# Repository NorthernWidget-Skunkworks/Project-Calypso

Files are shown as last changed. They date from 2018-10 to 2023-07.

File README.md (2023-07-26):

# Project-Calypso
The hardware and software designs for a turbidity measurement system, based on the work of a 2018 UMN senior design team

## Project Summary

Our team developed an open-source sensor to measure water turbidity. Turbidity, or "murkiness", increases when the water carries more sediment. Dissolved compounds can also increase turbidity by reducing water clarity. In general, less suspended and dissolved material makes better drinking water. Anyone may download and build this sensor (Design: https://doi.org/10.5281/zenodo.8177929).

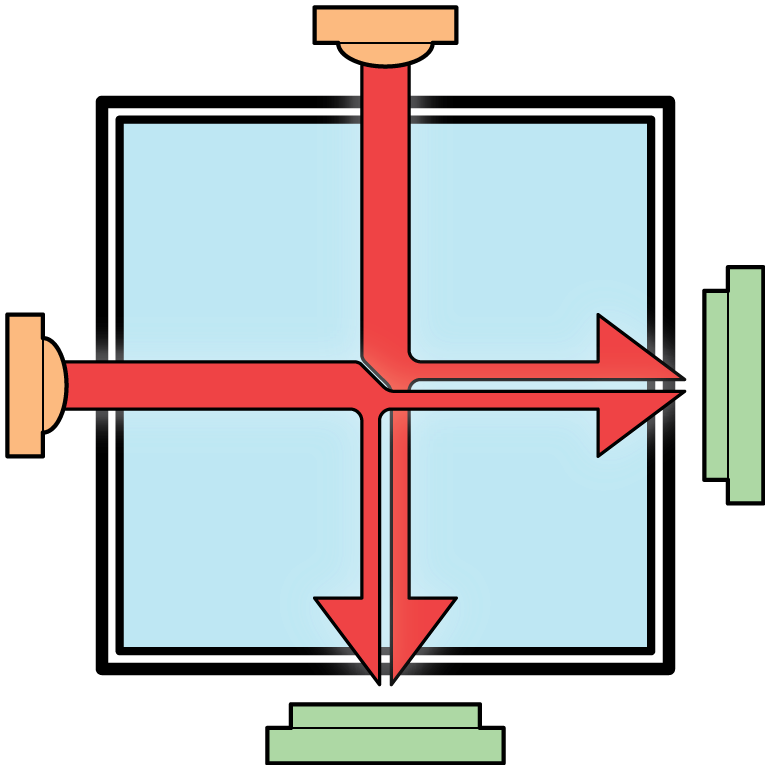
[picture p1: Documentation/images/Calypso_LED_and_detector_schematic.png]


*Two LEDs, red and infrared, send beams across the water to be measured, which lies within a transparent tube. These LED beams interact with the water, which reduces transmission and increases sidewas scatter. The detectors record both changes.*

The sensor, called "Project Calypso", shines lights from two LEDs through the water. These LEDs lie at right angles from each other along a clear square plastic tube. Detectors record the LEDs' brightness. The sensor directly across from each LED records light transmission. The sensor at 90 degrees from each LED records light scattering. Sediment in the water blocks the light and reduces transmission. Light can reflect off of sediment and scatter onto the sensor at 90 degrees. The scattering pattern depends on the wavelength of the light and sediment size. Therefore, we use both visible (red) and infrared light to learn about sediment size. Dissolved material reduces light transmission but does not scatter the light sideways. Because of this, Project Calypso can differentiate between sediment and dissolved compounds.

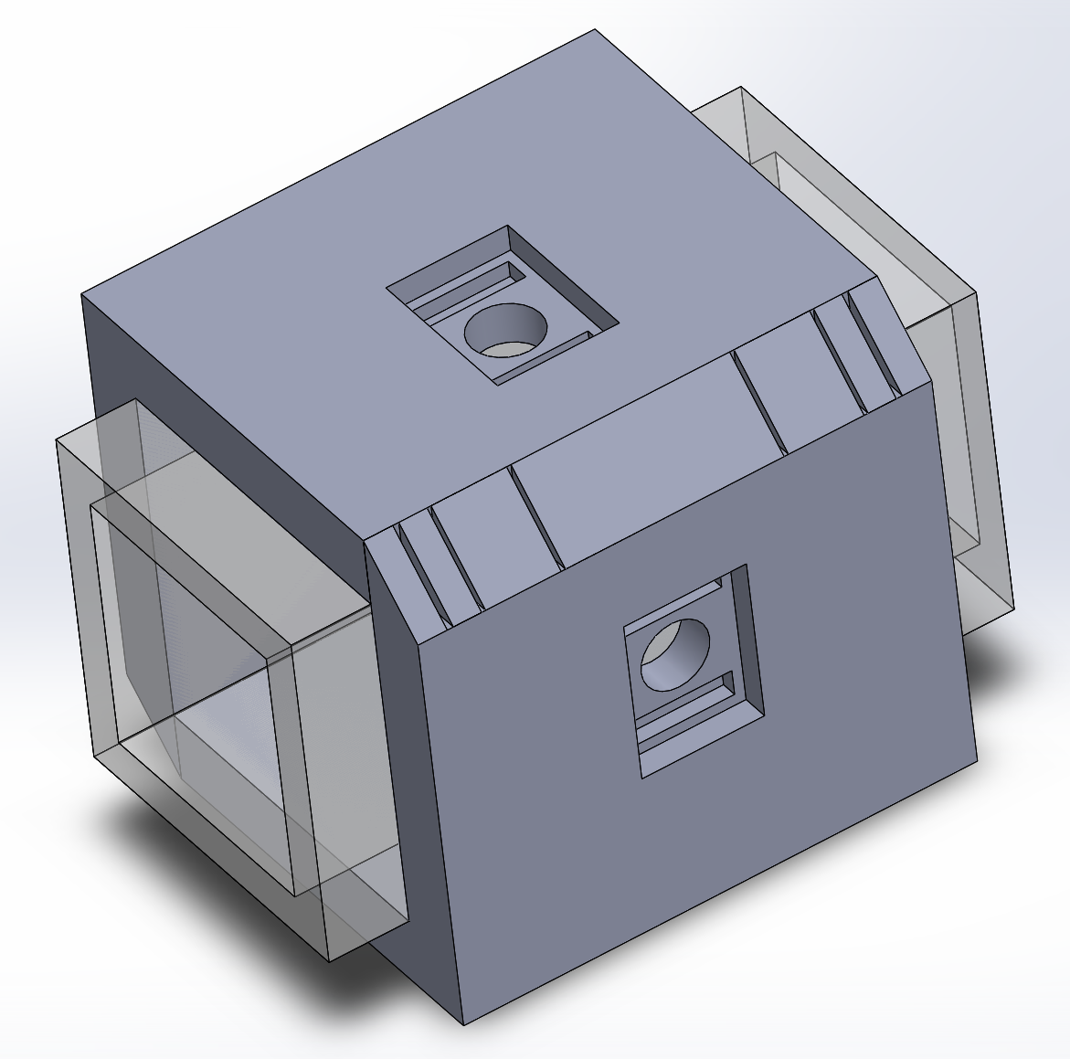
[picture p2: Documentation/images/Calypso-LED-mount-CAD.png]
CAD drawing of the LED and detector mount


*CAD drawing of the LED and detector mount. Sensors and mount surround a transparent plastic tube with a square cross section. Water, along with any suspended and/or dissolved matter that it carries, fills this tube.*

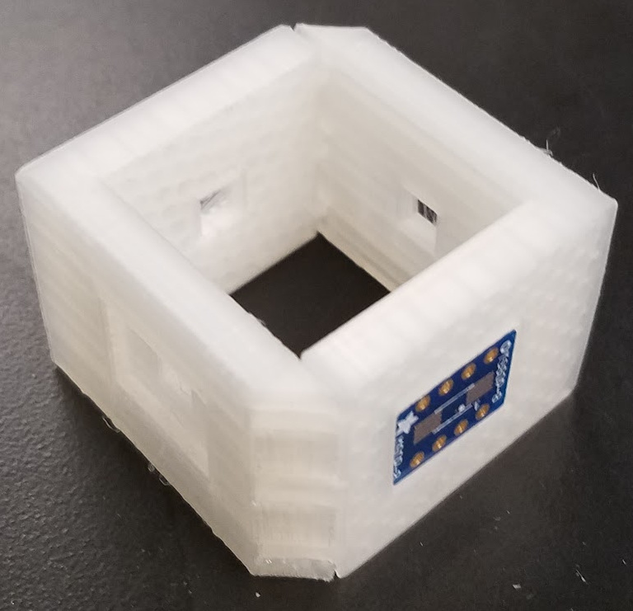
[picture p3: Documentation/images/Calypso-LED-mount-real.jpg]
Image of the LED and detector mount, including installed circuit boards.


*3-D printed LED and detctor mount, along with one of the installed custom circuit boards to hold the LEDs and light detectors.*

We characterized the Calypso sensor using standards of known turbidity. Sensor response varied systematically with water cloudiness and light wavelength. The Calypso turbidity-sensor system is not only an open-source alternative. It also provides more information than standard turbidity sensors.

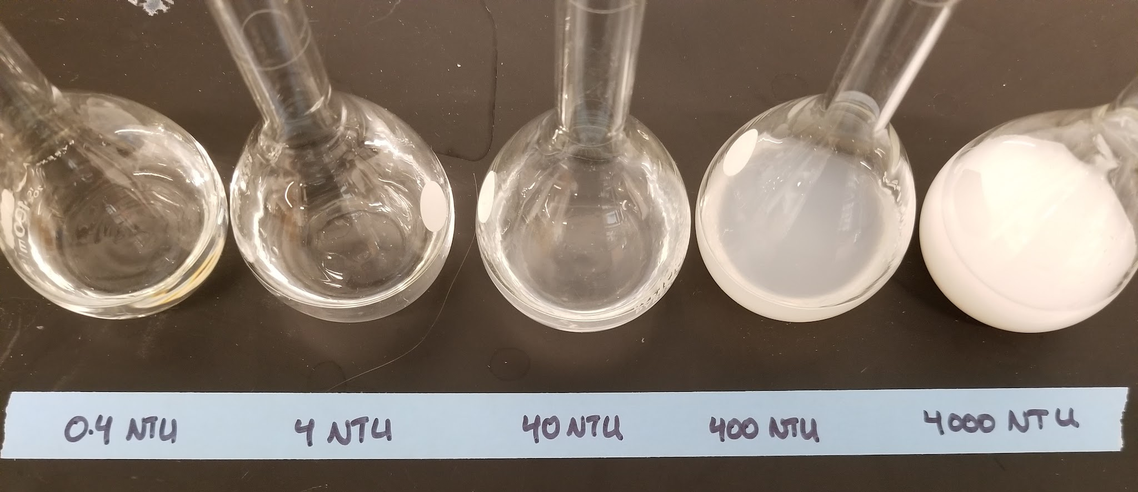
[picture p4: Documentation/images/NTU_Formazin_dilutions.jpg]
Increasing concentrations of Formaizin (left to right), with water becoming systematically cloudier.


*Increasing concentrations of Formaizin (left to right) cause the water to become systematically cloudier. We characterized the sensor using these standards.*

## Funding Support

Funding for this work came from the ***University of Minnesota Water Resources Center***, with support from the **USGS WRRI** program. This funding supported a grant to Wickert, Sandell, and Karwan, for their proposal entitled, *Open-Source Turbidity Sensor to Monitor Suspended and Dissolved Matter in Surface Water*.

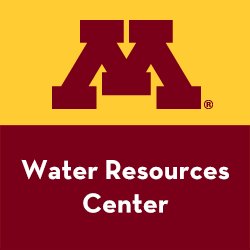
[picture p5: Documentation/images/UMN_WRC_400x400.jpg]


<br/>
<br />This work is licensed under a <a rel="license" href="http://creativecommons.org/licenses/by-sa/4.0/">Creative Commons Attribution-ShareAlike 4.0 International License</a>.

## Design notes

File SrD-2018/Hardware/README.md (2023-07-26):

# Senior Design 2018

Design files for the functional prototype designed by the student team and led by Bobby Schulz, Andy Wickert, Chad Sandell, and Diana Karwan.

Students:
* Corbin Buechler
* Amanda Hayden
* Aaron Nightingale
* Sean Rogers
* Erik Sundberg
* Jacob Wolf

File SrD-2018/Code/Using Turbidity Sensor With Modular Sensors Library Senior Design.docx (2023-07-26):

Turbidity Sensor & Modular Sensors Library

By Aaron Nightingale (night030@umn.edu)

Summary:

The turbidity sensor made for the spring 2018 senior design project can communicate with any device running the modular sensors library (like the MayFly data logger). This is accomplished using the “Turbidity.h” and “TurbidityHelper.h” classes. This document will describe how to set up this sensor with the modular sensors library. In addition, this document will explain various functions in each class, and how to use them.

Adding a Turbidity Sensor

This section will walk you through adding a turbidity sensor to the data logger code. See “MayFly-Logging => turbidity_logging => turbidity_logging.ino” for an example of using the turbidity sensor with the modular sensors library on the MayFly data logger (In the “Code Backups” folder on the Google drive).

1. Change the logging interval to be 10 minutes or more. For example:

const float loggingInterval = 10.0;

2. Include the “Turbidity.h” and “TurbidityHelper.h” classes:

#include "Turbidity.h"

#include "TurbidityHelper.h"

3. Add these constants to define the sensor’s address and the power pin:
  - Note: The turbidity sensor’s slave I2C address can be changed by altering the code found in “turbidity_slave.ino”.

uint8_t Turbidityi2c_addr = 0x08;

const int I2CPower = 22;

4. Create new “Turbidity” and “TurbidityHelper” objects as follows:
  - Note: The turbidity class had to be split up into two separate classes. This is because the turbidity sensor logs 7 different variables, and there is a limit of 4 variables per class in the modular sensors library.

Turbidity ntu01(I2CPower, Turbidityi2c_addr);

TurbidityHelper ntu02(I2CPower, Turbidityi2c_addr);

5. Add the following objects to the “variableList” array. These will be logged to an SD card.

new Turbidity_FS(&ntu01),

new Turbidity_SS(&ntu01),

new Turbidity_DARK(&ntu01),

new Turbidity_NTU(&ntu01),

new TurbidityHelper_FS(&ntu02),

new TurbidityHelper_SS(&ntu02),

new TurbidityHelper_DARK(&ntu02),

6. Congratulations! The turbidity sensor is now ready to be used with the MayFly. Upload the program to the MayFly, and connect the turbidity sensor to the data logger as shown in figure 1 below:

Data Logger Connection | Turbidity Sensor Connection | Purpose
+3.3v | Red | Sensor power
GND | Black | Sensor ground
(SDA) | Blue | I2C data line
(SCL) | Yellow | I2C clock line
N / A | Green | Sensor busy pin (Optional)

Figure 1 - Connections between the data logger and the turbidity sensor

“Turbidity.h” Class Reference

Summary

The “Turbidity.h” class is responsible for reading data from the turbidity sensor, telling the turbidity sensor to take a new measurement (update), and logging four of seven variables. This class is used in conjunction with “TurbidityHelper.h” to log all of the turbidity sensor’s data. The constants and functions in this class are described below:

Constants

- #define TURBIDITY_NUM_VARIABLES 4
  - This defines the number of variables in the “Turbidity.h” class. These four variables will be logged to an SD card.
- #define TURBIDITY_WARM_UP_TIME_MS 100
  - This defines the number of milliseconds necessary for the turbidity sensor to properly start up. 100ms was chosen as a “safe guestimate”.
- #define TURBIDITY_STABILIZATION_TIME_MS 0
  - This is the stabilization time for the turbidity sensor. This is unused in our setup.
- #define TURBIDITY_MEASUREMENT_TIME_MS 1000
  - This parameter defines the measurement time of the sensor. The default value of 1s was used.
- #define TURBIDITY_FS_RESOLUTION 2
  - This parameter sets the precision of the logged variable. In this case, the Turbidity_FS variable will be logged as a float with 2 digits past the decimal point.
- #define TURBIDITY_FS_VAR_NUM 0
  - This constant defines which variable is in position 0 of the variable array. In this case, the forward scattered light variable (from LED #1) is in position 0.
- #define TURBIDITY_SS_RESOLUTION 2
  - This parameter sets the precision of the logged variable. In this case, the Turbidity_SS variable will be logged as a float with 2 digits past the decimal point.
- #define TURBIDITY_SS_VAR_NUM 1
  - This constant defines which variable is in position 1 of the variable array. In this case, the side scattered light variable (from LED #1) is in position 1.
- #define TURBIDITY_DARK_RESOLUTION 2
  - This parameter sets the precision of the logged variable. In this case, the Turbidity_Dark variable will be logged as a float with 2 digits past the decimal point.
- #define TURBIDITY_DARK_VAR_NUM 2
  - This constant defines which variable is in position 2 of the variable array. In this case, the dark counts variable (from sensor #1) is in position 2.
- #define TURBIDITY_NTU_RESOLUTION 2
  - This parameter sets the precision of the logged variable. In this case, the Turbidity_NTU variable will be logged as a float with 2 digits past the decimal point.
- #define TURBIDITY_NTU_VAR_NUM 3
  - This constant defines which variable is in position 3 of the variable array. In this case, the turbidity variable (NTU) is in position 3.
- #define DATA_LEN 6
  - This constant defines the size of the response from the turbidity sensor. The turbidity sensor sends 6 float-type variables, causing the data length constant to be 6.
- #define COMMAND_LEN 7
  - The data logger can send various commands to the turbidity sensor. The commands are sent as a character array, and the length of said array is 7 bytes. Note that the last byte must be a zero.
- #define RES_DARK1 0
  - The turbidity sensor returns an array of 6 float-type variables to the datalogger. The float at position 0 of this array is the number of dark counts from sensor #1. The units for this are Hertz.
- #define RES_TRAN1 2
  - The turbidity sensor returns an array of 6 float-type variables to the datalogger. The float at position 2 of this array is the number of transmission counts from LED #1. The units for this are Hertz.
- #define RES_SCAT1 3
  - The turbidity sensor returns an array of 6 float-type variables to the datalogger. The float at position 3 of this array is the number of side scatter counts from LED #1. The units for this are Hertz.
- #define RES_DARK2 1
  - The turbidity sensor returns an array of 6 float-type variables to the datalogger. The float at position 1 of this array is the number of dark counts from sensor #2. The units for this are Hertz.
- #define RES_TRAN2 4
  - The turbidity sensor returns an array of 6 float-type variables to the datalogger. The float at position 4 of this array is the number of transmission counts from LED #2. The units for this are Hertz.
- #define RES_SCAT2 5
  - The turbidity sensor returns an array of 6 float-type variables to the datalogger. The float at position 5 of this array is the number of side scatter counts from LED #2. The units for this are Hertz.

Class Members

- uint8_t _i2cAddressHex;
  - This variable contains the I2C address of the turbidity slave sensor.
- char command[COMMAND_LEN];
  - This array contains the command that will be sent to the turbidity sensor. This array is a character array.
- float response[DATA_LEN];
  - This array contains the response from the turbidity sensor. This array consists of 6 float-type variables. Using these 6 variables, the turbidity of the water can be calculated. The variable at each position of the array is given by the “RES_XXX” constants. (Note that RES stands for RESponse array).

Class Methods

- Turbidity(int powerPin, uint8_t i2cAddressHex = 0x08, int

measurementsToAverage = 1);

  - This is the constructor for the “Turbidity.h” class. In this function, the “i2cAddressHex” variable is saved to the “_i2cAddressHex” member variable.
- bool wake(void) override;
  - This function is executed whenever the sensor is “waked” after a period of being idle. This function basically makes sure the sensor is powered on, and that the sensor has waited the proper warm up time.
- SENSOR_STATUS setup(void) override;
  - This function is executed whenever the sensor is set up for the first time. This function doesn’t do anything, and only returns the value of “getStatus()”.
- SENSOR_STATUS getStatus(void) override;
  - This function makes sure that the sensor is powered on. Then, this function checks to make sure that there is an I2C slave device at the “_i2cAddressHex” address. If there are any errors in either of these processes, the “SENSOR_ERROR” flag is returned. If the sensor was set up successfully, the “SENSOR_READY” flag is returned.
- String getSensorLocation(void) override;
  - This function returns a string containing the I2C address of the sensor. For example, “I2C_0x08”.
- bool addSingleMeasurementResult(void) override;
  - This function begins by calling the “sensorRead()” function. This function fills the “response[]” array with the current measurements from the turbidity sensor. Next, the values from the response array are copied to the “sensorValues[]” array. This allows the readings to be logged later. Afterwards, the “updateCommand()” is called to tell the sensor to take a new reading. This measurement process takes up to 8 minutes. Finally, the function returns true upon completion.
- bool sensorPresent();
  - This function verifies that a sensor is present at the current I2C address specified by the variable “_i2cAddressHex”. If a sensor is not present, this function returns false. If a sensor is present, the function returns true.
- void sensorRead();
  - This function reads data from the slave turbidity sensor over I2C. This is done in a byte by byte process, and the results are stored in the float-type “response[]” array.
- void sensorWrite();
  - This function sends the contents of the “command[]” array to the slave turbidity sensor. By changing the contents of the “command[]” array, different commands can be sent to the turbidity sensor. For example, if the array consists of “{‘U’,’P’,’D’,’A’,’T’,’E’,0}, then the update command is issued and the turbidity sensor begins taking a new measurement.
- void updateCommand();
  - This function sets the contents of the “command[]” array to be {‘U’,’P’,’D’,’A’,’T’,’E’,0}. Then the “sensorWrite()” function is called to send the update command to the turbidity sensor. This command tells the turbidity sensor to start taking a new measurement.
- float calculate_turbidity(float data[6]);
  - The “response[]” array should be passed to this function. This function calculates the turbidity using the data in the “response[]” array. The turbidity is returned as a float-type variable. This function can be changed to more accurately calibrate the turbidity sensor.

“TurbidityHelper.h” Class Reference

Summary

The turbidity sensor needs to log 7 variables to an SD card. However, the modular sensors library only allows 4 variables to be logged per sensor. To get around this, the “TurbidityHelper.h” class is used. This class is responsible for logging the side scatter counts from LED #2, the forward transmission counts from LED #2, and the dark counts from sensor #2. This class is very similar to the “Turbidity.h” class.

Constants

- #define TURBIDITY_HELPER_NUM_VARIABLES 3
  - This constant defines the number of variables that will be logged to an SD card using the modular sensors library.
- #define TURBIDITY_HELPER_WARM_UP_TIME_MS 100
  - This parameter defines the warm up time (in milliseconds) for the turbidity sensor. The default value of 100ms was used.
- #define TURBIDITY_HELPER_STABILIZATION_TIME_MS 0
  - This parameter defines the stabilization time (in milliseconds) for the turbidity sensor. The default value of 0ms was used.
- #define TURBIDITY_HELPER_MEASUREMENT_TIME_MS 1000
  - This constant defines the measurement time in milliseconds. The default value of 1s was used.
- #define TURBIDITY_HELPER_FS_RESOLUTION 2
  - This constant defines how many digits will be after the decimal point when saving the forward scattered light measurement to an SD card.
- #define TURBIDITY_HELPER_FS_VAR_NUM 0
  - This constant defines which variable is in position 0 of the variable array. In this case, the forward scatter counts variable (from LED #2) is in position 2.
- #define TURBIDITY_HELPER_SS_RESOLUTION 2
  - This constant defines how many digits will be after the decimal point when saving the side scattered light measurement to an SD card.
- #define TURBIDITY_HELPER_SS_VAR_NUM 1
  - This constant defines which variable is in position 1 of the variable array. In this case, the side scatter counts variable (from LED #2) is in position 1.
- #define TURBIDITY_HELPER_DARK_RESOLUTION 2
  - This constant defines how many digits will be after the decimal point when saving the dark counts measurement to an SD card.
- #define TURBIDITY_HELPER_DARK_VAR_NUM 2
  - This constant defines which variable is in position 2 of the variable array. In this case, the dark counts variable (from sensor #2) is in position 2.
- #define DATA_LEN 6
  - This constant defines the size of the response from the turbidity sensor. The turbidity sensor sends 6 float-type variables, causing the data length constant to be 6.
- #define RES_DARK1 0
  - The turbidity sensor returns an array of 6 float-type variables to the datalogger. The float at position 0 of this array is the number of dark counts from sensor #1. The units for this are Hertz.
- #define RES_TRAN1 2
  - The turbidity sensor returns an array of 6 float-type variables to the datalogger. The float at position 2 of this array is the number of transmission counts from LED #1. The units for this are Hertz.
- #define RES_SCAT1 3
  - The turbidity sensor returns an array of 6 float-type variables to the datalogger. The float at position 3 of this array is the number of side scatter counts from LED #1. The units for this are Hertz.
- #define RES_DARK2 1
  - The turbidity sensor returns an array of 6 float-type variables to the datalogger. The float at position 1 of this array is the number of dark counts from sensor #2. The units for this are Hertz.
- #define RES_TRAN2 4
  - The turbidity sensor returns an array of 6 float-type variables to the datalogger. The float at position 4 of this array is the number of transmission counts from LED #2. The units for this are Hertz.
- #define RES_SCAT2 5
  - The turbidity sensor returns an array of 6 float-type variables to the datalogger. The float at position 5 of this array is the number of side scatter counts from LED #2. The units for this are Hertz.

Class Members

- uint8_t _i2cAddressHex;
  - This variable contains the I2C address of the turbidity slave sensor.
- float response[DATA_LEN];
  - This array contains the response from the turbidity sensor. This array consists of 6 float-type variables. Using these 6 variables, the turbidity of the water can be calculated. The variable at each position of the array is given by the “RES_XXX” constants. (Note that RES stands for RESponse array).

Class Methods

- Turbidity(int powerPin, uint8_t i2cAddressHex = 0x08, int

measurementsToAverage = 1);

  - This is the constructor for the “Turbidity.h” class. In this function, the “i2cAddressHex” variable is saved to the “_i2cAddressHex” member variable.
- bool wake(void) override;
  - This function is executed whenever the sensor is “waked” after a period of being idle. This function basically makes sure the sensor is powered on, and that the sensor has waited the proper warm up time.
- SENSOR_STATUS setup(void) override;
  - This function is executed whenever the sensor is set up for the first time. This function doesn’t do anything, and only returns the value of “getStatus()”.
- SENSOR_STATUS getStatus(void) override;
  - This function makes sure that the sensor is powered on. Then, this function checks to make sure that there is an I2C slave device at the “_i2cAddressHex” address. If there are any errors in either of these processes, the “SENSOR_ERROR” flag is returned. If the sensor was set up successfully, the “SENSOR_READY” flag is returned.
- String getSensorLocation(void) override;
  - This function returns a string containing the I2C address of the sensor. For example, “I2C_0x08”.
- bool addSingleMeasurementResult(void) override;
  - This function begins by calling the “sensorRead()” function. This function fills the “response[]” array with the current measurements from the turbidity sensor. Next, the values from the response array are copied to the “sensorValues[]” array. This allows the readings to be logged later. Finally, the function returns true upon completion.
- bool sensorPresent();
  - This function verifies that a sensor is present at the current I2C address specified by the variable “_i2cAddressHex”. If a sensor is not present, this function returns false. If a sensor is present, the function returns true.
- void sensorRead();
  - This function reads data from the slave turbidity sensor over I2C. This is done in a byte by byte process, and the results are stored in the float-type “response[]” array.

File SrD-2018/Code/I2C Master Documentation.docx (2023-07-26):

I2C Master Documentation

By Aaron Nightingale (night030@umn.edu)

Summary:

The program titled “i2c-master.ino” is a bare-bones program that enables an Arduino to act as an I2C master device, and request readings from the turbidity sensor (slave device). This program is much easier to understand than the “Turbidity.h” and “TurbidityHelper.h” classes which are based on the modular sensors library. This program was frequently used when testing the turbidity sensor.

Using This Program

This program was used to test the turbidity sensor and do simple demonstrations. This program is intended to be programmed to an Arduino, which acts like a master device. Using this program, the Arduino can tell the turbidity sensor to take a new reading and display the results of that measurement on the serial monitor.

1. To use this program, upload it to a 3.3v Arduino device. (Note that 5v Arduinos could be used as well, but a level shifter is required. Figure 1 shows the type of level shifter that was used in our preliminary prototyping).
  - NXP has great documentation on I2C level shifters. General purpose N-Channel MOSFETS like the 2N7000 can be used. See the following website for more information:
  - https://www.nxp.com/docs/en/application-note/AN10441.pdf
2. Next, unplug the Arduino from the computer, and connect it to the turbidity sensor. The connections are shown in figure 2 below.
3. Verify the connections, and plug the Arduino back into the computer.
4. Select the serial port corresponding to the master Arduino. Then open the serial monitor and set the baud rate to 9600 bit/s.
5. You should see “Sensor #8 found.” displayed on the serial monitor. If not, double check the wiring, and make sure that the turbidity sensor is programmed with the “turbidity_slave.ino” program.
6. Various commands can now be sent to the turbidity sensor. For example, type “UPDATE” into the text box of the serial monitor and press enter. This will tell the turbidity sensor to take a new turbidity measurement.
7. The measurement process takes about 8 minutes. Once it is complete, the measurement results are displayed on the serial monitor. This includes the calculated water turbidity in NTU.
8. Now the turbidity sensor is up and running, and communicating with an I2C “master” Arduino!

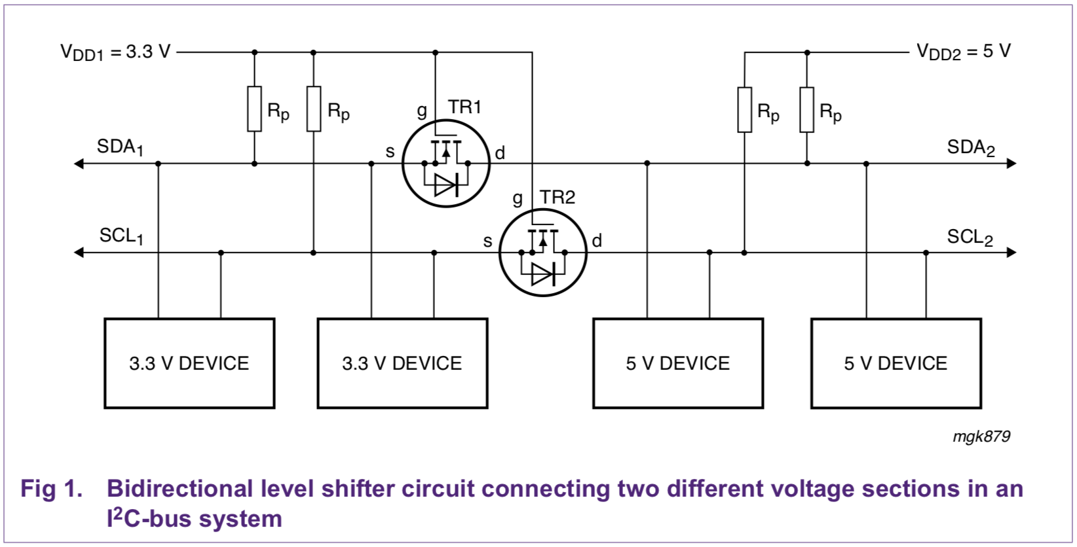
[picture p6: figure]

Figure 1 - I2C level shifter circuit

Master Arduino Connection | Turbidity Sensor Connection | Purpose
+3.3v | Red | Sensor power
GND | Black | Sensor ground
A4 (SDA) | Blue | I2C data line
A5 (SCL) | Yellow | I2C clock line
N / A | Green | Sensor busy pin (Optional)

Figure 2 - Connections between the I2C master Arduino and the turbidity sensor

“i2c-master.ino” Reference

Constants

- #define SLAVE_ADDR 8
  - This constant defines the address of the turbidity sensor. If the address of the turbidity sensor is changed in “turbidity_slave.ino”, then this constant must be changed to properly communicate with the turbidity sensor.
- #define DATA_LEN 6
  - This constant defines the size of the response from the turbidity sensor. The turbidity sensor sends 6 float-type variables, causing the data length constant to be 6.
- #define COMMAND_LEN 7
  - The data logger can send various commands to the turbidity sensor. The commands are sent as a character array, and the length of said array is 7 bytes. Note that the last byte must be a zero.
- #define RES_DARK1 0
  - The turbidity sensor returns an array of 6 float-type variables to the datalogger. The float at position 0 of this array is the number of dark counts from sensor #1. The units for this are Hertz.
- #define RES_TRAN1 2
  - The turbidity sensor returns an array of 6 float-type variables to the datalogger. The float at position 2 of this array is the number of transmission counts from LED #1. The units for this are Hertz.
- #define RES_SCAT1 3
  - The turbidity sensor returns an array of 6 float-type variables to the datalogger. The float at position 3 of this array is the number of side scatter counts from LED #1. The units for this are Hertz.
- #define RES_DARK2 1
  - The turbidity sensor returns an array of 6 float-type variables to the datalogger. The float at position 1 of this array is the number of dark counts from sensor #2. The units for this are Hertz.
- #define RES_TRAN2 4
  - The turbidity sensor returns an array of 6 float-type variables to the datalogger. The float at position 4 of this array is the number of transmission counts from LED #2. The units for this are Hertz.
- #define RES_SCAT2 5
  - The turbidity sensor returns an array of 6 float-type variables to the datalogger. The float at position 5 of this array is the number of side scatter counts from LED #2. The units for this are Hertz.

Global Variables

- char command[COMMAND_LEN];
  - This array contains the command that will be sent to the turbidity sensor. This array is a character array.
- float response[DATA_LEN];
  - This array contains the response from the turbidity sensor. This array consists of 6 float-type variables. Using these 6 variables, the turbidity of the water can be calculated. The variable at each position of the array is given by the “RES_XXX” constants. (Note that RES stands for RESponse array).

Functions

- void setup()
  - This is the setup function of the I2C master program. In this function, the I2C bus and the serial port are initialized. After that, the function checks to see if there is a turbidity sensor connected to the I2C bus using the “sensorPresent()” function.
- void loop()
  - This is the main loop of the program. The function begins by reading the current values of the sensor using the “sensorRead()” function. Next, this data is displayed on the serial monitor using the “dumpFormattedData()” function. Afterwards, the program waits until the user has entered a command into the serial monitor. If a valid command is entered, then this command is sent to the turbidity sensor using I2C. In most cases, the “UPDATE” command is sent to the turbidity sensor, causing it to take a new turbidity reading. This measurement process takes about 8 minutes, so an 8 minute delay is added to this function. Then, the function loops back to the start and repeats.
- void getSerialCommand()
  - When this program is running, and the master Arduino device is connected to a computer, then the user may send commands to the turbidity sensor using the serial monitor. This function reads data from the serial monitor and puts it into the “command[]” array. For example, if a user types “UPDATE” into the serial monitor, then this function parses that string into a character array {‘U’,’P’,’D’,’A’,’T’,’E’,’0’}, which can be sent to the turbidity sensor using I2C.
- bool sensorPresent(int addr)
  - This function checks if there is a sensor present at the desired address. This function is used before any data transactions with the turbidity sensor. TRUE is returned if an I2C sensor was found at the specified address.
- void sensorRead()
  - This function requests data from the turbidity sensor using I2C. The turbidity sensor sends 6 float-type variables one byte at a time. This function reads the data from the turbidity sensor, byte by byte, and stores this data in the “response[]” array.
- void sensorWrite()
  - This function sends the contents of the “command[]” array to the slave turbidity sensor. By changing the contents of the “command[]” array, different commands can be sent to the turbidity sensor. For example, if the array consists of “{‘U’,’P’,’D’,’A’,’T’,’E’,0}, then the update command is issued and the turbidity sensor begins taking a new measurement.
- void debug(int i)
  - This is a basic function that is used for debugging. When this function is called, “DEBUG: #” is written to the serial monitor, where the value if the argument “i” is represented by the # sign.
- void dumpSensorData()
  - This function dumps the contents of the “response[]” array to the serial monitor. Each float is displayed on a new line. This function was primarily used for debugging purposes.
- float calculate_turbidity()
  - This function calculates the turbidity using the data in the “response[]” array. The turbidity is returned as a float-type variable. This function can be changed to more accurately calibrate the turbidity sensor.
- void dumpFormattedData()
  - This function dumps the contents of the “response[]” array to the serial monitor. However, unlike the “dumpSensorData()” function, this function displays a short description of what each number is. This function was used for debugging and simple demonstrations of the turbidity sensor.

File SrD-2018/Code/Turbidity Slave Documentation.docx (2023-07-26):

Turbidity Slave Documentation

By Aaron Nightingale (night030@umn.edu)

Summary:

This program contains the code for a turbidity sensor. The turbidity sensor is an I2C slave device, and can communicate with another Arduino or data logger using I2C. This turbidity slave program contains functions that measure the transmitted light, scattered light, and the dark counts from each light-to-frequency sensor. In addition, this program has functions that average these readings and sends them to a master I2C device.

Using This Program

1. Open the “turbidity_slave.ino” program in the Arduino IDE.
2. Next, upload this program to a 3.3v compatible ATMega328 chip.
  - Notice: You may need to burn the bootloader to the chip first. See the following link for details on how to do that:
  - https://www.arduino.cc/en/Tutorial/ArduinoToBreadboard
3. Once the program has been uploaded to the chip, connect the chip to the turbidity sensor circuitry. (Schematics of this circuitry can be found in the following Google Drive folder: “Turbidity Sensor Senior Design 2018” => “Final Documentation”)
4. Double check the circuit connections.
5. Now the turbidity sensor is ready to be used! Connect the turbidity sensor to a 3.3v Arduino running the “i2c-master.ino” program to view the turbidity measurements.
  - For reference, the connections are shown in figure 1 below:
  - See “I2C Master Documentation” PDF for more details on how to set this up.

Master Arduino Connection | Turbidity Sensor Connection | Purpose
+3.3v | Red | Sensor power
GND | Black | Sensor ground
A4 (SDA) | Blue | I2C data line
A5 (SCL) | Yellow | I2C clock line
N / A | Green | Sensor busy pin (Optional)

Figure 2 - Connections between the I2C master Arduino and the turbidity sensor

“turbidity_slave.ino” Reference

Constants

- #define SLAVE_ADDR 8
  - This constant defines the address of the turbidity sensor. If the address of the turbidity sensor is changed in “turbidity_slave.ino”, then this constant must be changed to properly communicate with the turbidity sensor.
- #define DATA_LEN 6
  - This constant defines the size of the response from the turbidity sensor. The turbidity sensor sends 6 float-type variables, causing the data length constant to be 6.
- #define COMMAND_LEN 7
  - The data logger can send various commands to the turbidity sensor. The commands are sent as a character array, and the length of said array is 7 bytes. Note that the last byte must be a zero.
- #define SENSOR1 2
  - This parameter defines the pin that is connected to sensor #1. (Light to frequency sensor #1).
- #define SENSOR2 3
  - This parameter defines the pin that is connected to sensor #2. (Light to frequency sensor #2).
- #define L1_HIGH 5
  - This parameter defines the pin that controls when LED #1 is turned on.
- #define L1_OFF 6
  - This constant defines the pin that controls when LED #1 is turned off.
- #define L2_HIGH 7
  - This parameter defines the pin that controls when LED #2 is turned on.
- #define L2_OFF 8
  - This constant defines the pin that controls when LED #2 is turned off.
- #define BUSY 13
  - This constant defines the location of the busy pin. This pin is held high when the turbidity sensor is busy taking a new measurement. The turbidity sensor should not be interrupted over I2C while a measurement is in progress.
- #define TYPES 6
  - This parameter defines the size of the array which stores the measurement results. The turbidity sensor measures 6 different parameters, which are stored in the “result[]” array.
- #define REPEATS 5
  - This parameter defines the number of measurements that should be averaged for each new reading.
- const char MODE01[] = {'M','O','D','E','0','1',0};
  - This constant defines the “MODE01” I2C command. This command is not implemented in the turbidity sensor, but can be used as an example of how to implement custom I2C commands into the program.
- const char MODE02[] = {'M','O','D','E','0','2',0};
  - This constant defines the “MODE02” I2C command. This command is not implemented in the turbidity sensor, but can be used as an example of how to implement custom I2C commands into the program.
- const char MODE03[] = {'M','O','D','E','0','3',0};
  - This constant defines the “MODE03” I2C command. This command is not implemented in the turbidity sensor, but can be used as an example of how to implement custom I2C commands into the program.
- const char UPDATE[] = {'U','P','D','A','T','E',0};
  - This constant defines the “UPDATE” command. This command tells the turbidity sensor to take a new turbidity reading.

Global Variables

- char command[COMMAND_LEN];
  - This array contains the command that will be sent to the turbidity sensor. This array is a character array.
- volatile uint8_t go;
  - This variable stores the number of seconds remaining in the frequency measurement process.
- volatile uint32_t count;
  - This variable stores the number of rising edges that were counted on the interrupt pin.
- float measurements[TYPES][REPEATS]
  - This array holds all of the measurements from the light to frequency sensors. The “TYPES” dimension corresponds to the different measurements, while the “REPEATS” dimension corresponds to separate sets of measurements. The “REPEATS” dimension is usually 5, meaning that 5 measurements are averaged. The average of the measurements in this array is stored in the “result[]” array, which is then sent to the data logger.
- float result[TYPES];
  - This array contains the response from the turbidity sensor. This array consists of 6 float-type variables. Using these 6 variables, the turbidity of the water can be calculated. The contents of this array are sent to the I2C master device (data logger) over I2C in a byte by byte process.
- bool needsUpdate;
  - This variable is TRUE whenever the sensor needs to take a new measurement. Long functions cannot be used in the I2C interrupt routines, which is why this variable is used.

Functions

- void setup()
  - This function is run before the main loop. It initializes the I2C interface and sets up the timers used for measurements. The input and output pins are set in this function as well.
- ISR(TIMER1_COMPA_vect)
  - This is an interrupt service routine for timer #1 within the Arduino microcontroller. This routine is called whenever the value in the timer register is equal to the value of some compare register. This function is used to measure the counts on the light to frequency sensors for some duration of seconds.
- void freq_counter()
  - This function is also an interrupt routine, and is called whenever there is a rising edge on some pin. This function simply increments the “count” variable with each rising edge. This function can be used on different pins of the Arduino microcontroller using the “attachInterrupt()” function.
- void LED1_OFF()
  - This function sets the “L1_OFF” pin high in order to turn LED #1 off.
- void LED1_LOW()
  - This function sets LED #1 to the low-intensity setting. This is done by setting the “L1_OFF” pin and the “L1_HIGH” pin low.
- void LED1_HIGH()
  - This function sets LED #1 to the high-intensity setting. This is done by setting the “L1_HIGH” pin high and setting the “L1_OFF” pin low.
- void LED2_OFF()
  - This function sets the “L2_OFF” pin high in order to turn LED #2 off.
- void LED2_LOW()
  - This function sets LED #2 to the low-intensity setting. This is done by setting the “L2_OFF” pin and the “L2_HIGH” pin low.
- void LED2_HIGH()
  - This function sets LED #2 to the high-intensity setting. This is done by setting the “L2_HIGH” pin high and setting the “L2_OFF” pin low.
- uint32_t SENSE1(uint8_t seconds)
  - This function reads the pulses from light-to-frequency sensor #1. The pulses are counted for a time duration specified in the argument of the function. The number of pulses counted is returned as an unsigned 32 bit integer.
- uint32_t SENSE2(uint8_t seconds)
  - This function reads the pulses from light-to-frequency sensor #2. The pulses are counted for a time duration specified in the argument of the function. The number of pulses counted is returned as an unsigned 32 bit integer.
- float READ_SENSOR1()
  - This function uses the “SENSE1()” function to calculate the frequency of the pulses from sensor #1. The frequency of the pulses from light-to-frequency sensor #1 is returned as a float-type variable.
- float READ_SENSOR2()
  - This function uses the “SENSE2()” function to calculate the frequency of the pulses from sensor #2. The frequency of the pulses from light-to-frequency sensor #2 is returned as a float-type variable.
- float SENSOR1_DARK()
  - This function turns each LED off, and measures the frequency from light-to-frequency sensor #1. The frequency is returned as a float-type variable.
- float SENSOR2_DARK()
  - This function turns each LED off, and measures the frequency from light-to-frequency sensor #2. The frequency is returned as a float-type variable.
- float LED1_TRANSMISSION()
  - This function measures the transmitted light from LED #1. This is done by setting LED #1 to be in the low intensity mode. This is accomplished using the “LED1_LOW()” function. Afterwards, the frequency is measured using the “READ_SENSOR1()” function. The intensity of the transmitted light is proportional to the frequency of the light-to-frequency sensor, which is returned as a float-type variable in hertz.
  - Note: Increasing the brightness of the LED can cause the light-to-frequency sensor to produce more pulses than the microcontroller can handle. For this reason, the LED has a low intensity mode.
- float LED1_SCATTER()
  - This function measures the 90˚ side-scattered light from LED #1. To do this, LED #1 is set to operate in the high-intensity mode. This is done by calling the “LED1_HIGH()” function. Next, the frequency of the light-to-frequency sensor is measured using the “READ_SENSOR2()” command. The intensity of the side-scattered light is proportional to the frequency of the light-to-frequency sensor, which is returned as a float-type variable in hertz.
- float LED2_TRANSMISSION()
  - This function measures the transmitted light from LED #2. This is done by setting LED #2 to be in the low intensity mode. This is accomplished using the “LED1_LOW()” function. Afterwards, the frequency is measured using the “READ_SENSOR2()” function. The intensity of the transmitted light is proportional to the frequency of the light-to-frequency sensor, which is returned as a float-type variable in hertz.
  - Note: Increasing the brightness of the LED can cause the light-to-frequency sensor to produce more pulses than the microcontroller can handle. For this reason, the LED has a low intensity mode.
- float LED2_SCATTER()
  - This function measures the 90˚ side-scattered light from LED #2. To do this, LED #2 is set to operate in the high-intensity mode. This is done by calling the “LED2_HIGH()” function. Next, the frequency of the light-to-frequency sensor is measured using the “READ_SENSOR1()” command. The intensity of the side-scattered light is proportional to the frequency of the light-to-frequency sensor, which is returned as a float-type variable in hertz.
- void measure()
  - This function measures the dark counts, transmitted light, and the side scattered light from each light-to-frequency sensor. This is a total of 6 frequency measurements, which are saved to the “measurements[][]” array. These measurements are repeated several times, as specified by the “REPEATS” constant. In our setup, 5 sets of measurements are taken each time that this function is called.
- void average()
  - This function calculates the average frequency of each of the 6 different frequency measurements (dark counts, transmission, side scatter, etc.). The average values are saved to the “result[]” array, and are later sent to the data logger over I2C.
- void requestEvent()
  - This function is an interrupt service routine for the I2C interface. This function is called whenever the master device requests data from the turbidity sensor. This function sends the contents of the “result[]” array, byte by byte, to the master device using the I2C interface.
- void receiveEvent(int howMany)
  - This function is an interrupt service routine for the I2C interface. This function is called whenever the master sends data to the turbidity sensor. The data logger can send various commands to the turbidity sensor. This function interprets and executes the received command.
  - The only command that is implemented right now is the “UPDATE” command. When the turbidity sensor receives the character array corresponding to this command over I2C, the “needsUpdate” variable is set to be true. This causes the turbidity sensor to take a new set of measurements.
- void loop()
  - This is the main loop of the turbidity sensor program. In this loop, the turbidity sensor takes a new set of measurements if the “needsUpdate” variable is true. After the new measurements are taken and averaged, the “needsUpdate” variable is set to false. This loop waits 1ms and then repeats itself.

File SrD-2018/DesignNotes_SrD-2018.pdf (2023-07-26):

Solidworks Models: The final models are included in a seperate folder with some easy to open images. The curves are visual approximations, however, most of the dimensions are direct from the manufacturer. The gasket wasn’t modeled. The 3D printed part is the same as the final one Bobby sent. The 45 degree angle cut of the 3D printed part isn’t necessary should the hole for the acrylic tube be moved slightly further away from the short edge of the box. Ideally, one should use the black filament version of the one Bobby was using to keep reflections to a minimum. ABS is not recommended due to warping and worse tolerancing.

Breakout Boards: The final breakout boards, though slightly more expensive, had pads that better fit the LEDs and IR sensors. They were also smaller and had only 6 pins instead of the 8 from the Adafruit.

Measurement Routine: The turbidity sensor collects a total of six measurements: Sensor 1 dark, Sensor 2 dark, LED 1 transmission, LED 1 side scatter, LED 2 transmission, and LED 2 side scatter. The dark measurements are collected with both LEDs off to determine the amount of ambient light present to use as a baseline for the other measurements. In all of our code and documentation LEDs and Sensors are numbered so that LED 1 faces Sensor 1, and LED 2 faces Sensor 2. Therefore, the LED 1 transmission measurement is collected by Sensor 1 and its side scatter is collected by Sensor 2, and so on.

Since the sensors can output a maximum frequency of almost 600 kHz, but the ATmega329P microcontroller can only count edges on a signal up to 75 kHz (when it is clocked at 8 MHz), the SN74HC393N binary counter sits between the sensors and the microcontroller to effectively divide the incoming frequencies by 8. While this configuration allows the full range of the light sensors to be utilized, it also introduces a potential error since the microcontroller is only counting every eighth rising edge. This error is inversely proportional to the number of edges that are counted, so low frequencies are most affected. To address this, the functions controlling the measurement process make adjustments to try to receive at least 100 edges for each sample, which ensures an error of less than one percent.

For each measurement, the microcontroller first samples the sensor output for one second. If it receives 100 or more edges (corresponding to frequencies of 800 Hz and higher), it accepts this value. If it receives less than 100 edges, it determines the amount of time needed to receive 100 edges, with some additional headroom, and samples again for this extended amount of time. For example, if the microcontroller receives 37 pulses in one second, it will repeat for three seconds on the second pass. If less than three pulses are received in the first pass, the second pass is collected for the maximum length of two minutes. This will allow the microcontroller to detect frequencies as low as 5.87 Hz with a 1% error maximum error. As will be discussed below, this will correspond to a maximum expected collection time of about 8.5 minutes. If it is preferred to collect data more often, the maximum sampling time can be reduced at the expense of some precision. For example, if the maximum sampling time is reduced to one minute or 30 seconds, the minimum frequency detected at 1% error or less would be increased to 11.73 Hz or 27.47 Hz, respectively, with maximum expected collections times of about 4.5 minutes and 2.5 minutes, respectively.

Since the two dark measurements are the only ones that tend to be below the 800 Hz threshold, and are therefore the primary drivers of the collection length, they are not collected as often as the other four measurements in a cycle. The routine begins by collecting each of the two dark measurements, followed by five passes of the other four (two transmission and two side scatters), and then finishes with another collection of the two dark measurements. This means that there are a total of four dark measurements, which can take up to two minutes each depending on the amount of ambient light present, plus twenty transmission and side scatter measurements, which are very rarely longer than one second each. This results in the roughly 8.5 minute maximum collection time mentioned above. The six sets of measurements are then averaged so that only six values are reported to the data logger. The data logger computes the conversion to NTU and logs this value along with the six that were reported by the sensor.

Calibration Process: To calibrate the sensor, we collected measurements using six samples of varying turbidity - deionized water (treated as 0.0004 NTU for fit lines), 0.4 NTU, 4 NTU, 40 NTU, 400 NTU, and 4000 NTU. In the accompanying “Calibration” folder, we have provided the raw data from these measurements. The resulting best fit lines from our calibration process are listed below. Due to some saturation/non-linear behavior in our data, certain sections of the curves were not used to generate the fit lines. Since the side-scatter from LED 1 is fit from 0.0004 NTU to 400 NTU, this frequency value is used by the conversion function to determine what range of turbidity we are dealing with and therefore which formulas should be calculated and averaged to determine the NTU value.

LED 1 Side Scatter for < 4 NTU
NTU = 10^((freq-4884.51015963563)/(217.615730769231))

LED 1 Side Scatter for 4-400 NTU
NTU = (freq-4723.4758127632)/(112.799965681699)

LED 1 Transmission for > 400 NTU
NTU = exp((freq-905841.461548272)/(-108472.245937816))

LED 2 Side Scatter for 4-400 NTU
NTU = (freq-6696.20138888889)/(79.3873036786787)

LED 2 Transmission > 400 NTU
NTU = exp((freq-601607.276911029)/(-71291.2384864573))

Before applying these formulas, the dark measurement taken from the corresponding sensor is subtracted from the transmission or side scatter measurement. For example, if an LED 2 side scatter measurement is 10,160.00 Hz, and the Sensor 1 dark measurement is 73.85 Hz, then the difference, 10,086.15 Hz, is used in the NTU conversion formula. We determined that this is an accurate method for controlling for ambient light by measuring each calibration sample five times with regular lighting conditions and five times with an additional light shining into the turbidity sensor’s tube. We found that the dark and transmission/side scatter measurements from collected from a light sensor would increase by the same number of hertz, with the difference between them remaining constant.

Possible Extension - LEDs Supplied by Current Sources: As Bobby has brought up, an alternative to our design with fixed resistors setting the current through the LEDs would be to implement a digitally or PWM controlled current source to drive the LEDs instead. This would allow the light intensities to be adjusted after a sensor is constructed, which would not only help with tuning an individual sensor to maximize its accuracy but would also be able to address variations from unit to unit due to the manufacturing process once the sensors are being produced in larger quantities. We did not get a chance to look into this alternative extensively during the semester and have not identified any specific hardware to implement, but if we were going to continue working on this project, this would be the next direction that we would explore.

Possible Extension - LEDs of Different Wavelengths: Since our design essentially collects redundant data from the two identical light sources, a possible extension would be to experiment with changing the wavelength of one of the LEDs. While researching the light sources recommended for measuring turbidity, we found that that the 860 nm wavelength that we implemented works best for the most common particle size of interest. By using a different wavelength with one of the LEDs, the sensor could measure the turbidity due to two different particle sizes in the water. We were not able to find any other wavelength recommendations, so we do not know if it would be most useful to increase or decrease the wavelength or by how much, but we believe that this is another possible area where the sensor’s capability could be improved with some additional research.

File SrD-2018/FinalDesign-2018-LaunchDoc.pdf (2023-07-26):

### Turbidity Sensor Product Launch Document

University of Minnesota
EE 4951W
May 2, 2018

Group Members:
Corbin Buechler
Amanda Hayden
Aaron Nightingale
Sean Rogers
Erik Sundberg
Jacob Wolf

Advisors:
Professor Joseph Talghader - Electrical and Computer Engineering Professor Andrew Wickert - Department of Earth Sciences Anthony Aufdenkampe - Senior Environmental Scientist, LimnoTech

Abstract/Summary

Turbidity, the cloudiness or haziness of a fluid, is a major symptom of water pollution in all bodies of water, and it is only getting worse. Detecting water turbidity levels in remote locations is challenging and expensive, and it is often not feasible. Our team has developed a portable and inexpensive turbidity sensor that will work with multiple open source data loggers. The crucial components of the sensor include its waterproof housing, the light source, light detecting circuitry, and the software responsible for relaying data to the open source data logger. After these individual parts were designed, they were integrated into a final product that can be left in remote locations for data acquisition. Researchers hope that this sensor will be able to be reproduced on a larger scale to help monitor and mitigate turbidity levels in rivers, lakes, streams, and perhaps even drinking water in developing countries.

Introduction

This paper addresses the following areas of the project; motivation, objectives and customer requirements, technical background, design and description, team organization, overall goals, future improvements, timeline, and budget. The motivation for the project is simple, to develop a low cost and portable turbidity sensor that can be used with multiple open source data loggers and be deployed for lengthy periods of time. The technical background gives the reader an understanding of what a turbidity sensor is and how it operates. The design and description includes details of development of the main parts of the design. The first major component being the LED and sensor circuit that contains the light to frequency converters and software that correlates the frequency to some turbidity measurement. The second major component being the I2C communications interface between our sensor and the data logger. The third major component is the circuit design and layout. In particular, the LEDs and sensors had to be accurately positioned in order to optimize the light passing through the acrylic tube. The last major component is the waterproof housing and cable, as well as the overall integration of each component. In regards to team organization, we chose to delegate different components of the project to each person. Although each person was responsible for a different part of the project, there was a lot of collaboration in order to integrate the final product. The goal of the project very closely followed the initial specifications and requirements of the client. Although the project was successful, there are some changes that could be implemented if the design were to be reproduced, mostly having to do with time and monetary constraints. As for the timeline, the integration of all parts began the last week in March to allow significant time for testing and calibration that were to be completed by May 1st. The development costs came in under budget, at around $750. In addition, the final sensor design costs less than $100, as requested.

Motivation

Given that Minnesota has thousands of lakes and streams, water turbidity is a serious problem locally. However, measuring it is difficult. There is not enough time and resources to test all bodies of water. Sensors that are available are expensive, often costing over $1,000. To make matters worse, most commercial sensors are designed to be used in a lab setting, meaning researchers and scientists cannot take measurements in the field. Lab sensors also require calibration using special solutions, which significantly increases the cost. The sensors that can give real-time readings are even more expensive, so much so that it is not fiscally viable for a company to purchase more than one or two of these units. This project proposed the development of a low-cost turbidity sensor that can be field deployed in remote locations. In turn, this sensor will help quantify and mitigate the effect of practices that lead to contamination and soil loss. Our turbidity sensor uses low amounts of power, and can be powered from a solar cell in field testing situations. The turbidity sensor also communicates with an open-source data logger, which saves the turbidity readings onto an SD card. This allows researchers to have access to real-time turbidity readings without having to bring samples or the sensor back to the lab. All of the designs for this turbidity sensor are open-source, allowing other researchers to build their own turbidity sensor and continue the development of the design. When the design and documentation is made available, this project could lead to massive changes in environmental research and protection.

Objectives and Customer Requirements

The main goal of this project is to create a working turbidity meter, loosely following a design provided by the client. The sensor shall use light scattering and transmission to measure the turbidity of water. The clients currently use two different data-loggers for field measurements. Another goal of this project was to write code that interfaced our sensor with these open source data loggers. The client required that all sensor and communications code must be open-source for future changes and use.
The client provided several overall project specifications as well. First, a working turbidity sensor must be developed, prototyped, and delivered to the client by the end of the semester. In addition, the fully operational sensor must be shown at the senior design show. The sensor should be able to correctly read the turbidity of various liquids in a blind test. The clients would provide us with a budget of $1,000. We were expected to get approval and place all purchases through their lab, with the exception of minor circuit components, which could be obtained from the ECE Depot if possible.
Because the client would like to use this sensor in the field, there are several important specifications for the device itself. Foremost, it must be enclosed in a rugged, waterproof enclosure that can withstand up to three months of deployment in typical bodies of water. For that reason, it must be IP68 rated. For example, it must be able to withstand currents pushing it around and any possible impacts from debris churned up during storms or other events. It must have the minimum power consumption possible for prolonged operation. The enclosure must also be able to handle depths of up to three meters. The sensor is being powered from a solar panel mounted on a central box nearby. There are other instruments inside this box that also draw power. It is important that our sensor does not overload this box. Our client uses sensors that draw a maximum of 50 mA, so the current consumption of our sensor should be below that. The sensor must operate on 5 and/or 3.3 volts, as that is the only power provided from the box. The sensor itself must use a light source (LED or laser) to measure scattering at different angles and transmission, in order to better calculate the NTU of the water in question. The sensor code within must be modeled in Arduino in order to be compatible the data loggers. All final code must be open source as well. Calibration, using standard turbidity liquids must be performed, and should be done in a lab setting. The sensors will report readings in Nephelometric Turbidity Units (NTU) with an accuracy of 3%. The target price per sensor should be less than $100. Diana Karwan, the co-lead client for this project, would like to test a unit in the field in April, depending on weather.
The client has also requested several pieces of paperwork along with a working sensor. First, they would like a bill of materials in order to see a breakdown of required parts and costs to manufacture several sensors. Next, they have also requested instructions on how to build the sensor. These must be simple enough so that anyone can follow them. Along with the instructions, the clients would like information regarding important design decisions made throughout the project. This will make it easier for the client to make further changes or improvements, based on difficulties we experienced during our development and prototyping.

Technical Background

The most commonly used unit of measurement for turbidity is the Nephelometric Turbidity Unit (NTU). Turbidity is determined by shining a beam of light through the liquid sample and measuring the amount of light that is scattered at some angle. The most common arrangements measure 90 degree side-scattering, backscattering, which is the light reflected back toward the source, or transmission, which is the light that passes through the sample in a straight line from the source. Many commercial turbidity meters measure only a single direction of light scattering, which can perform well in measuring low turbidity samples but are less accurate past a certain threshold NTU. In more turbid conditions, the light may be scattered multiple times, causing less of it to reach the sensor, which would be interpreted as a decrease in turbidity. By measuring both light scattering and transmission, a sensor can take accurate readings over a wider range of turbidity values. As discussed below, our sensor measures the light transmitted and the light scattered at 90 degrees from two different light sources.

Detailed Design Description

The exterior of the turbidity sensor consists of a waterproof aluminum box with a square acrylic water inlet tube mounted horizontally through the enclosure. Two infrared LEDs and two light intensity sensors are mounted around this square tube so that each LED faces one of the sensors. This arrangement allows the sensors to pick up the transmitted light and the 90 degree side-scattered light from each of the light sources. The LEDs used in our design have a wavelength of 860 nm, which was chosen to comply with the ISO 7027 standard for measuring turbidity. For light detection, we decided to use a pair of integrated circuits that senses light and outputs a square wave what a frequency that is proportional to the light intensity. These signals are collected by an ATmega328P microcontroller, which counts the number of rising edges over a period of time to determine the frequency. In most cases, this measurement is taken over one second, but it can be extended to up to two minutes to ensure that very low frequencies are counted accurately. Since the light sensors can output frequencies up to nearly 600 kHz, while the microcontroller’s interrupts can only reach up to 75 kHz, the light sensors’ outputs are routed through a pair of binary counters that effectively divide the output frequencies by eight before they reach the microcontroller’s inputs. This process introduces a potential error when collecting low frequency signals, but this is minimized by extending the sampling period in these cases.
In addition to capturing the outputs from the light intensity sensors, the ATmega chip also turns the LEDs on and off at the appropriate times. Since the maximum side-scattered light from a source is significantly less than the maximum transmitted light, we have developed a circuit that can light up each LED at a higher and a lower intensity to use as much of the light sensors’ range as possible. The sensing routine first measures the amount of ambient light present by measuring the outputs of each sensor with both LEDs off. Next, it turns one LED on with a low intensity, and capture the transmitted light data from the sensor directly across from it. Next, that same LED is turned up to the higher intensity, and side-scattered light data will be read from the other sensor, positioned at a 90 degree angle. This is then repeated for the other LED source. This process repeats five times for each of these four lights measurements followed by a final ambient light measurement. These six collected values are then each averaged and stored until they can be sent to the connected data logger via I

2C.
The turbidity sensor can be connected to either the ALog or Mayfly data loggers. Every ten minutes, the data logger tells turns the turbidity sensor on, and requests the current turbidity readings using an I2C interface. The data logger these collected frequency values to a corresponding NTU value. The algorithm that does this was developed by measuring a selection of liquid samples with known turbidities. This NTU value, along with the six frequency measurements, are saved to an SD card on the data logger. After this, the data logger turns the turbidity sensor off and waits a certain amount of time for the next data point.
One of the more complicated aspects of the physical design was the mounting of the LEDs and IR light to frequency sensors. We used surface mount light sensors and LEDs, which made it difficult to mount on the four sides of the acrylic tube. In addition, these components had to be aligned in order for the turbidity sensor to work properly. We developed a 3D printed shell that would go around the acrylic tube. This shell consisted of two parts, which allowed the sensors and LED to be mounted on the back side of the part. This left a flat surface facing the side of the tube. This part can hold the LEDs and IR sensors in place, is very low cost, and is easily reproducible given the SolidWorks software model.
To mount the LEDs and IR sensors electrically, we used a small breakout board. It can take the surface mounted LEDs and IR sensors and convert them to 0.1” pins, which we connected to wires that go to the microcontroller. Using two 3D printed parts that attached together around the tube, with each part housing an LED and an IR sensor, turned out to be very easy to mount in place. These 3D printed parts were attached to the tube using an adhesive glue. In addition, that same adhesive glue held the LEDs and IR sensors inset upon the 3D part. To prevent possible short circuits, we put tape over the exposed parts of the sensors and the wires.
The waterproof enclosure and cable assemblies are some of the most crucial elements. The IP68 enclosure is from PolyCase, and is made of cast aluminum. This enclosure will not deteriorate when submerged in water. The square water inlet tube is made of acrylic for the same reason. In addition, it is clear, and will not deflect the light from the LED as to distort any data being measured. Another major benefit of this enclosure is the integrated rubber gasket, which creates a seal around the lid. In order to guarantee that the sensor enclosure sunk, a small square piece of granite was attached to the inside, underneath the circuit board. The plugs connecting the sensor to the cable are IP68 rated, and are designed for continuous submersion. The female panel mount plugs are not permanent when attached, so they can be moved from one enclosure to another without issue. This was ideal for testing and calibration. For power and communications, we used an insulated 6-conductor PVC cable. The insulation also will not degrade in water. The 6 conductors will be for power (2), communications (2), controls(1), and one extra left unconnected. Each cable has a male plug attached at one end, which then connects to its female pair on the box. All joints around the plugs and inlet tube are sealed with marine-grade silicone caulk. Because the aluminum boxes were expensive, several plastic boxes from the ECE Depot were used for initial testing and prototyping. This way, we could make several changes to the design or box construction without exhausting our budget. These boxes were made waterproof by applying silicone caulk around cuts made in the box.
This project met or exceeded a significant amount of its goals. Most significantly, we kept cost well below $100 per sensor. For one sensor, the price is just under $89. However, if the client or another customer would like to build as many as 100 at a time, the price would become $54 per sensor. Any construction methods or other cost limiting strategies available to the customer would drive prices down even further. Next, the sensor had to be deployable for up to 3 months running on solar power alone. Because of this, our target current consumption was 50 mA. Our sensor, while running at maximum power during a measurement routine, consumes 6.6 mA. The client can integrate our sensor into their system without any concerns about power. While we aren’t able to prove the sensor is waterproof for up to three months, all components are rated for such deployments. We are confident the sensor will maintain its integrity at depths of up to 10 feet for three months. All components also have specified operating temperature ratings that easily span our specified temperature range of 0-30°C. Given the structural integrity of the box and low power consumption, it is possible the sensor could be deployed for longer than three months. Also note that the sensor was calibrated with known turbidity solutions. As a result, we have met our accuracy requirements. Further testing and calibration would only increase the accuracy of the sensor.

Overall, this project met nearly all of its goals. There were only two major goals that were not met. First, one of the major specifications was to build a sensor that was field deployable for up to three months. Given the timeline of the project and the school semester, testing this was simply not possible. That being said, all of our enclosure and cable components are rated to be waterproof for extended submersion. However, these ratings are not absolute and do not guarantee to be waterproof for days or months. Secondly, we did not use lab grade turbidity standards when calibrating our sensor. Again, this is because of the limited time and resources available to us during the semester. In addition, the inclement weather that extended into April severely hindered our ability to perform real world tests in various bodies of water nearby. We performed an adequate number of tests to obtain a curve of best fit over the range of turbidity levels that our sensor will subjected to.

Future Improvements

Since we could not fully test our turbidity sensor in a submerged environment until it was completely assembled, our circuit design had to be developed using a number of assumptions. One of these was the assumption that when the sensor was out of water, the amount of light transmitted from an LED to the light sensor directly across from it would be be the same or greater than the amount transmitted through clean deionized water or any more turbid sample. Following this assumption, the LED brightness for this measurement was scaled with enough headroom to account for additional ambient light leakage, like sunlight, plus a little more to err on the side of caution. However, when we began to calibrate our sensor, the transmission measurements for low to medium turbidities (DI water and 0.4-40 NTU samples) were significantly higher than what we measured when the sensor was out of water, with the sensors saturating at their maximum outputs. This did not prevent us for calibrating over the full range of turbidities, since the side-scatter measurements were reliable in this range, but if the LED intensities were scaled down, the transmission measurements could be used in combination with the side-scatter readings to develop a more robust and accurate NTU conversion algorithm.
Besides just adjusting the resistance in series with the LEDs to control their brightness, which is how our sensor functions, a possible re-design could use a constant current driver controlled by pulse width modulation (PWM) to supply the LEDs. This would come with some increase in the cost and complexity of the circuit, but would allow the LED intensities to be adjusted by simply re-programming the ATmega chip. Since our clients ultimately want to produce and sell these sensors, this would be particularly useful for adjusting for any variations between units in the manufacturing process. This solution would also likely require a custom PCB to fit within the enclosure. This would not be a problem for mass production, but due to our available timeline for our project, we were not able to explore this route for our design.
Although the 3D printed part was able to fit around the acrylic tube well and held the LEDs and IR sensors, some improvements could be made. The easiest improvement would be to print the part in black filament instead of the white filament that we used which needed to be spray painted black to keep the light reflections to a minimum. Simply buying the same filament that we used in black would be ideal. Additionally, the hole made for the acrylic tube would be moved slightly so that there would be more room to fit the 3D printed part around the tube. This would be especially helpful if the protoboard was made into a PCB, presumably making it smaller. A better adhesive could also be used for longer term stability for holding the two 3D printed parts together as well as holding the sensors and LEDs to said parts. These changes would improve the reproducibility of the sensor, however they would not have a direct impact on the measurements.
Although the housing, cabling and waterproofing aspects of the design are adequate for what we had specified, some improvements could be made if future sensors were to be created. First and foremost, additional long term testing could be done on the final enclosure over long periods of time to say definitively how long the product can be submerged. Given the limited timeline, there was not sufficient time for long term testing. Given the short term waterproof testing, it is clear that the enclosure is waterproof. Additionally, all components used in the design are individually rated to meet the specifications of the project. Another thing to consider is the cables and plugs used. Trying to keep the sensor cost low, cheaper plugs and cables were used. If more money were available for each unit ,it could be beneficial to purchase plugs that have a tighter locking mechanism. This would be helpful if the sensor were placed in turbulent waters with risk of the plug becoming detached. As far as the cable used on the project, if more money were allotted it would also be beneficial to use a rubber cable vs the semi-rigid PVC cable that was used simply because the rubber cable is less susceptible to wear from harsher environments. If the sensor were to be reproduced, another thing that could be done differently is to manufacture some mass for sinking the sensor. The piece of granite is not ideal as it is not manufactured to maximize space within the sensor, but was a cheap alternative for the sensor at hand. Again, if the budget allowed, the process could have been improved if the proper tools were purchased. Specifically, for cutting the opening in the enclosure to insert the acrylic tube.

Team Organization

Name | Role
Amanda Hayden | Team Lead, Housing
Corbin Buechler | LED and Sensor Code / Hardware
Aaron Nightingale | Data Logger Interface Code
Sean Rogers | Housing, Cabling, Waterproofing
Erik Sundberg | Hardware Layout, Mounting, 3D Modeling
Jacob Wolf | Optics / Hardware Integration

Budget

Our clients had an overall budget of $4,500 for this project, of which they allocated $1,000 for turbidity sensor development. However, they requested that sensor design and production be as inexpensive as possible, allowing for ongoing design and production. Below is a table of the overall costs associated with the development of the sensor over the semester. It is important to note that the working turbidity meter was delivered to the clients both under budget for development as well as under the target “per sensor” price of $100.

Subsystem | Amount spent
Waterproof Housing and Cabling | $125
Test Equipment | $300
Circuit Design Components | $200
Integrated Circuits and Microprocessors | $125
Total | $750

Updated Individual Effort Statement - Corbin Buechler

Since I came to this project without much prior knowledge about water quality and how it is measured, the first work I did was to research the common methods used to measure turbidity and to get an idea of how commercially available turbidimeters are built, hoping to gain some insight about how we could approach the physical form of our turbidity sensor. Since our clients specifically mentioned an interest in measuring light transmission in addition to the side- or back-scattering that is typically measured by commercial turbidimeters, we would need our design to allow for a light source and a sensor to be mounted facing each other with space for the sample in between. After sketching some ideas, I came up with and shared a drawing of a clear square tube passing through a standard rectangular enclosure, which is very close to the form that we ended up moving forward with.

After we developed an overall plan for our project, I volunteered to work on the LED and light sensor circuit and code. I began by identifying LEDs of the appropriate wavelength and sensors that would be easy to integrate without a lot of additional parts. After that, a large portion of my time was spent working on Arduino code that will let the ATmega328P accurately read the highest possible frequency from the light-to-frequency converters. Since the ATmega’s interrupts could only read up to about 75 kHz, while the sensors could output up to near 600 kHz, I added a pair binary counters between the sensors and the microcontroller to effectively divide the sensor’s output frequency by 8. Since the ATmega was only receiving every 8th pulse, this introduced an additional potential for error, which required me to reconfigure the sensing routine software to extend the sampling time when lower frequency signals were being received.

To maximize the useful range of the light sensors, I wanted to address the fact that the relatively low light produced by side-scattering (less than percent of the maximum transmission intensity) would only use a small portion of the light sensors’ frequency range, which could limit the accuracy of our side-scattering measurements. My solution was a scheme that allows each of our LEDs to be illuminated at two levels of intensity. This circuit uses two current limiting resistors in series with each LED. One of these resistors is connected on either end to the drain and source of a MOSFET, with the gate and source each connected to a pin on the microcontroller. The drain is connected in series with the other resistor, which connects on its other side to the LED’s cathode. In this configuration, the source pin controls whether the LED is on or off (turning it on when the pin is LOW and vice versa), and the gate pin controls whether a low or high current is allowed to flow through the LED. When the gate pin is LOW, the MOSFET is in the cutoff region and the two resistors in series allow the low current to flow. If the gate is set HIGH, the MOSFET turns on and shorts the second resistor, raising the LED current to produce a brighter light source for measuring side-scattering light.

Since our final design is powered by 3.3V supplied by the data logger, the ATmega328P to be clocked at or below 10 MHz. Our initial code development was being done on an Arduino Uno, which uses the same microcontroller, but is powered with 5V and clocked at 16 MHz. Since the Arduino IDE does not have native support for programming a standalone ATmega chip with an external 8 MHz crystal clock source, I needed to do some research to determine how we could do this.

Besides my main task of developing this code and circuitry, I also planned the layout of our circuit on perfboard and soldered the components together. During the calibration process, I took the frequency data that we collected while measuring samples of know turbidity and produced a set of fit lines to develop a calibration algorithm for determining the turbidity, in NTU, of an unknown sample.

Updated Individual Effort Statement - Amanda Hayden

When I initially came across this project, I was immediately intrigued. I did a quick Google search of ‘turbidity’ and found that it is a measure of cloudiness or haziness of a fluid due to suspended particles. I also knew I needed to further my understanding of the topic. I explored current sensor models and how the sensors worked, and came upon NTU, or Nephelometric Turbidity Units, and the mechanism that measures the turbidity. This is done by measuring the intensity of side- and back-scattered light in a sample of water, taking the frequency of the light and converting it to NTU based on the calibration data saved in the sensor memory. More research led to my understanding of common light sources and light sensors used in the device, which included LED’s, lasers, and light-to-frequency sensors, as well as an understanding of the open source code languages and programs used in these devices. The clients granted access to their Alog and Mayfly code for study and education purposes so I spent a good amount of time parsing through the code to understand the process.

After our initial meeting with the clients and advisors, the group determined that I would be the project lead. I checked in with each team member, submitted assignments, and communicated with the clients and advisors, as well as participating in the housing and waterproofing sub-team with Jake and Sean. Our initial picture of the final product came from Corbin, who had designed for a square tube for water flow to go through the instrument and for circuitry, the sensors, and light sources to surround it. All was going well until I suffered a concussion at the beginning of February, which sidelined me for a solid two weeks and only allowed for limited academic activity for some time after that. I am very thankful that my group was understanding of my situation, and that my limited contribution during the month of February to the housing and waterproofing team was actually useful.

Once my head was fully healed, I began by helping with selecting and creating the turbidity standard solutions for calibration. To save some money, we decided to order Formazin at 4000 NTU as our standard solution, and to practice our chemistry skills of dilution. Our client, Andy Wickert, has a lab in Tate Hall and he granted us access to use the deionized water for our calibrations. We requested a set of graduated cylinders, pipettes, a set of beakers, and a set of Nalgene bottles for storing our solutions. One of the cylinders was a two-milliliter syringe, which allowed for extremely precise measurements. Upon recommendation by Professor Wickert, our calibration solutions are spaced out on a logarithmic scale: 4000, 400, 40, 4, 0.4 NTU. Deionized water is 0 NTU, by definition.

The entire group was present for calibration and testing, and we all contributed to the poster, the final design paper, and the final presentation.

Updated Individual Effort Statement - Aaron Nightingale

After some initial brainstorming for the turbidity sensor project, I chose the role of developing software that allowed our sensor to interface with various data loggers. In the first few weeks of this project, I was focused on choosing a communications protocol. This was an important decision, because it influenced the circuit design and programming that was done later. To make a good decision, I skimmed through the ALog and MayFly data logger specifications to see what interfaces they supported. We had already decided that we would use an Arduino as the “brains” of our turbidity sensor. After all of this research, I decided that I2C would be the best communication protocol to interface our sensor with these data loggers. I2C is supported by Arduino software and has great documentation. In addition, the MayFly and ALog data loggers already have libraries that interface with other sensors over I2C. Using I2C as the communications interface significantly simplified the development of our turbidity sensor.
The next step in my software development plan was to create a working prototype of two devices communicating using the I2C protocol. To do this, I did a lot of research to learn more about how I2C worked. I also looked for example code from various online sources. By the middle of February, I had a firm understanding of I2C, and began writing two programs for two Arduino microcontrollers. The first program included code for an I2C “slave” device. In our case, the slave device is our turbidity sensor. The second program included code for an I2C “master”. In this case, the master is one of the previously mentioned data loggers. In the I2C master program, I included functions that the data logger would use, such as a function that would check if the sensor is present, a function that could send a command to the sensor, and a function that would request a data packet from the sensor. In the I2C slave program, I included functions that the turbidity sensor would use. This includes handling different commands from the master and sending a data packet with the current turbidity readings.
By the end of February, I had begun testing these I2C master / slave programs on two Arduino boards. Shortly thereafter, I had a working prototype of two Arduinos communicating with each other using I2C in a master / slave format. This prototype used a communication method that was almost identical to the data logger / turbidity sensor interface. This made it very easy to adapt this code to run on the ALog and Mayfly data loggers.
In March, the next step was to become familiar with the data logger source code. In the first three weeks of this month, I carefully examined the source code and learned how these data loggers operated. The data logger software was much more complex than I anticipated. The things that I learned in these three weeks allowed us to successfully interface our turbidity sensor with the data loggers later.
In accordance with the project timeline, the prototype code had to be adapted to run on the Mayfly and ALog data loggers in April. I did this by creating a new C++ class for our turbidity sensor. This class includes various different functions that the data logger uses to setup, get data, and send commands to the turbidity sensor. Because we already had a prototype of two microcontrollers communicating over I2C, adapting this code to run on the data loggers was a fairly straightforward process. After the data logger software was complete, I merged my I2C slave program with Corbin’s data acquisition program. I believe that developing these two programs separately was a wise decision, and allowed us to avoid some potential problems earlier in the project. These two programs were merged in late April, and once it was finished, we had a working turbidity sensor that was compatible with the ALog and MayFly data loggers.

Updated Individual Effort Statement - Sean Rogers
The first step for me was to do some basic research and find out exactly what the group was being asked to do. After meeting the group and advisors, we went home to brainstorm design ideas. Corbin brought a very cool design to our first team meeting, that we all immediately agreed on. We broke down what specific areas of the project needed handling, which would be enclosure and cabling, sensor code, data logger interface code, circuit design, and hardware integration. I chose the waterproof housing, cabling, and hardware integration. I was also in charge of most of the parts ordering.
My research of waterproofing led me to Ingress Protection (IP) ratings. They are an international standard used to define levels of sealing effectiveness of electrical enclosures against dirt and moisture intrusion. The rating consists of a two-digit number. Our enclosure, cabling, and outlets would need to be IP68 rated. This means it is dust tight and protected against complete, continuous submersion in water. My first research step was to find an enclosure and plugs that would suit our needs. I discovered PolyCase, a company that makes several different models of waterproof enclosures out of ABS or aluminum. They had a box that was the perfect size and affordable for our budget. We decided to buy several similar sized boxes from the Depot for testing and design purposes.Switchcraft has a line of plastic, waterproof plugs that were perfect for the project. We needed a male cable plug and a female panel mount plug. Each plug was specifically IP68 rated and did not require special installation. The next item was the actual cable running from the sensor to the central hub. We decided to use six-conductor cable – two for power, two for communications, and two extra. We agreed on a fifteen-foot length, but weren’t sure how the cable should be insulated. After some research, I discovered PVC would be okay. We found several cable options on DigiKey that were in budget. The first purchase had 28 AWG conductors, however, they were too small to properly solder. A few days later, Switchcraft launched a new line of waterproof plugs that were slightly bigger, had 24 AWG conductors, and were more sturdy. Finally, I had to consider the tube running through our enclosure. I found some square acrylic tube I could cut to length. It would not degrade or shrink in water. I decided we would use marine-grade silicone caulk to seal the area around the tube.
Jake and I tested the enclosures to make sure they were waterproof. We both constructed a box with a tube in place and no plug, and placed them in buckets over break. There were no leaks, therefore the tube and waterproofing was sound. I cut holes for the tube in the aluminum box using a Dremel tool. After securing the tube and sealing the edges, I tested it for leaks. It was completely dry after two days. Jake then drilled a hole for the plug. Again, we tested it and found no leaks. Next, I worked with Jake and Amanda to create our turbidity standard solutions. I worked with Bobby to order one liter of 4000 NTU solution that we would dilute to 400, 40, 4, and 0.4 NTU for testing. We did this by working in the lab with proper measuring equipment. We used deionized water to dilute the solutions to the necessary volume and stored them in nalgene bottles to be used when testing.
I began working with Erik to design and test a 3D part that would be a mount for our LEDs and sensors, which would sit on the tube. Erik printed an initial design that didn’t quite fit. With some experimentation, we found a design that could easily be glued to the tube.
Then, working with Bobby, I soldered the LED’s and sensors onto breakout boards. With his help and equipment, I completed the task without issue. As a group, we met in the design lab to attach the sensors to the 3D mount and attach those to the tube. I used hot glue to secure all the in place around the tube and make sure there wouldn’t be any shifting during use. Corbin then built the circuit and placed it in the box. Working with Jake, we soldered wires in place between the plug and circuit board. Our design was complete. The next phase was testing using the solutions I helped create earlier. This testing went off without issue. Corbin used the data to construct best fit curves that would be the basis of our sensors code. The final steps will be creating the project documentation for the client, designing our presentation poster, and verifying all code works with the data loggers. Most of this will be done as a group.

Updated Individual Effort Statement - Erik Sundberg

In the initial assignment of roles, I, as an electrical engineering major with little programming experience and a focus in power, thought it would be best to take on a hardware role within the project. As most of our team are electrical engineers with a power focus, I was happy to take on the more detailed role of interfacing the electrical hardware with the physical hardware. Initially, I helped design and provide feedback to the various preliminary designs of the sensor. Specifically, the layout of the box with respect to where the water would enter the acrylic tube, how the water would then be read from inside the box, and a general layout of the turbidity sensor’s insides.
After we had some general layout of the whole project, I wanted to have a visual model that we would be able to use for prototyping. Since the University offers Solidworks for free, I installed it and started learning how to navigate and create what we needed. After a few hours, I was able to make a simple box that looked vaguely like the box we had ordered. After a few more hours, I had the correct dimensions and was able to have both the tube inside the box and a top.
Once we had received parts, I helped and offered feedback to those working on the specific electrical hardware. This was, in one form, deciding the best way to mount the LEDs and IR sensors that would be surrounding the acrylic tube and taking measurements of the water. Initially, we decided on a four PCBs or perfboards solution where they would interlock at 90 degree angles around the tube. Though this was not ideal, we could not see a better alternative. In addition to the four PCBs or perfboards, we thought it could be reasonable to use a custom PCB for the main circuit. After exploring this option further by looking at the software Eagle, which only one of our group members had ever had exposure to, I thought it would be best to use four breakout boards for the surface mount components that our advisors wanted us to use. After trying one type of board somewhat successfully, I found a much better breakout board that was smaller and didn’t have additional, unnecessary terminals. Using the model I had created, I found the largest size perfboard that we would use for the main processor and circuit.
To hold these small boards in place, it was initially proposed we use liquid rubber. However, because this would require manual alignment with a large margin of error, I spent some time researching a better alternative. I eventually came up with the idea of using a 3D printed part that would house the breakout boards in a very specific orientation for much better accuracy and mounting ability. I went about creating something in Solidworks as it is the preferred method for printing 3D parts according to our supervisors. Because there was no datasheet that detailed the exact size of the small breakout boards, I estimated the size and created a model to put inside my existing model of the box and tube combination. After receiving the part, I was able to make an exact model of both the board and the 3D part that I designed. After conferring with my teammates, I refined my design from being one part that would slide around the tube, to being two parts that would join together around the tube. After printing this design, the other breakout board was found and chosen so I had to further redesign the 3D printed part. It was at this point that a total redesign was made. Instead of having the sensors mounted to the inside of the 3D printed part, I thought it would be best for easy mounting to have them attached on the back. Once printed, this design was used as it also provided a better fit against the acrylic tube.
After designing and refining the 3D printed part, I helped with the overall completion of the project. I helped with the calibration of the sensor to the known turbidity solutions and with the documentation of our project. I also helped by troubleshooting the few problems we had with the full sensor which included determining the issue of why some readings were off which was due to some resistors not being correctly sized for measuring very low turbidities. I helped with the poster and the final presentation as well as getting all the documentation in order for our clients to use when they build their own.

Updated Individual Effort Statement - Jacob Wolf

At the start of the project, I did a significant amount of research on existing turbidity sensor designs. I found that there are some commercial units available as well as small units that don’t contain microprocessors. I studied the circuit layout for the different types of sensors and researched different ways to detect transmission and scattering. I found that although there are different ways of implementing a turbidity sensor, and many different circuit layouts, they all essentially do the exact same function to perform a common task. The research gave me an understanding of how the overall design of the turbidity sensor should be and what we types of parts we should expect to have to make our sensor operational. I then focused more on learning how the scattering and forward transmission in infrared emitters and detectors worked and how we can use the light detection to actually measure turbidity.
The next task I focused on was determining how we could make the unit waterproof. Since we had decided on an approximate enclosure shape and type, I worked with Sean to determine an appropriate size. We decided on the size of the enclosure by looking at the approximate circuit size and layout with the sensor’s viewing window and cable termination inside the box. The goal was to then find a box of the approximate size we wanted that contained a watertight seal on the cover. Knowing that we will have to cut a hole in the enclosure for the acrylic tube, which will be the ‘viewing window’ for the sensor, we want everything else to be as watertight as possible. Sean and I found and decided to use an aluminum box that was the appropriate size and had a watertight seal (IP68 rated) for the lid. From there I worked again with Sean to determine the best method for waterproofing the enclosure. We decided to use marine grade silicone around any opening that we cut into the box. Additionally, after discussing with the other team members about the number of conductors we shall require in the cable to the data logger (for power and ground, communication, etc), I did some research to find cables and plugs that are waterproof. Additionally, I wanted to find a plug that we could disconnect from the unit but yet was secure enough that it would not come disconnected if the unit were put into fast moving waters and were jolted around. After acquiring the plugs and cables, I drilled the appropriate holes in the boxes to assemble the plugs and then proceeded to solder the cables to the plugs as well as conductors on the inside of the plug to connect to the circuit board. For additional waterproofing, I used silicone to install the watertight plug. I then painted the acrylic viewing window with a black epoxy paint to reduce light interference with our measurements. I then placed the acrylic tube in the enclosure and used the silicone to seal around all surfaces both inside and outside the enclosure. I cut a piece of granite to fit within the enclosure while still allowing room for the circuitry and wires. The granite had to be heavy enough to cause the sensor unit to sink but no so heavy that it would strain the cable. To test the waterproofing of the unit I then cut a hole in the ice on a pond and submerged the unit for several days at a depth of 10 feet, which is the max depth specified for the unit. The inside of the unit was dry when removed from the water, indicating that it was indeed waterproof.
The next action I took with Sean and Amanda was creating the testing liquids. Using the 4000 NTU solution that we ordered form HACH, we made serial dilutions following a log scale to the values of 400, 40, 4, and 0.4 NTU. These would be the solutions we use to take data, plot the data points, and ultimately create our line of best fit curves for converting the output frequency from our sensors to an NTU value. We then spent an afternoon as a group running the testing sequence with the various liquids we created to get a set of data points for our sensor calibration.
The last stages of the project include putting together all the documentation on the parts and methods used so that our clients can re-create the sensor. In addition, we put together our final design poster in preparation for the design show.

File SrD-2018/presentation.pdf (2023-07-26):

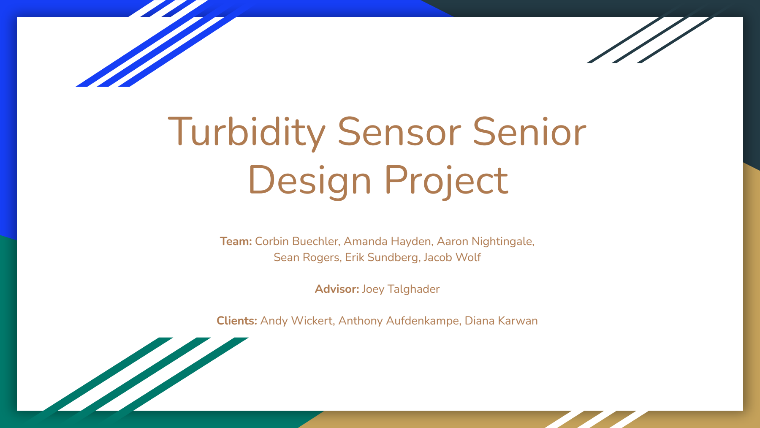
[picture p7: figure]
Turbidity Sensor Senior Design Project; Sean Rogers, Erik Sundberg, Jacob Wolf; Advisor: Joey Talghader

Team: Corbin Buechler, Amanda Hayden, Aaron Nightingale,

Clients: Andy Wickert, Anthony Aufdenkampe, Diana Karwan

# What is Turbidity?

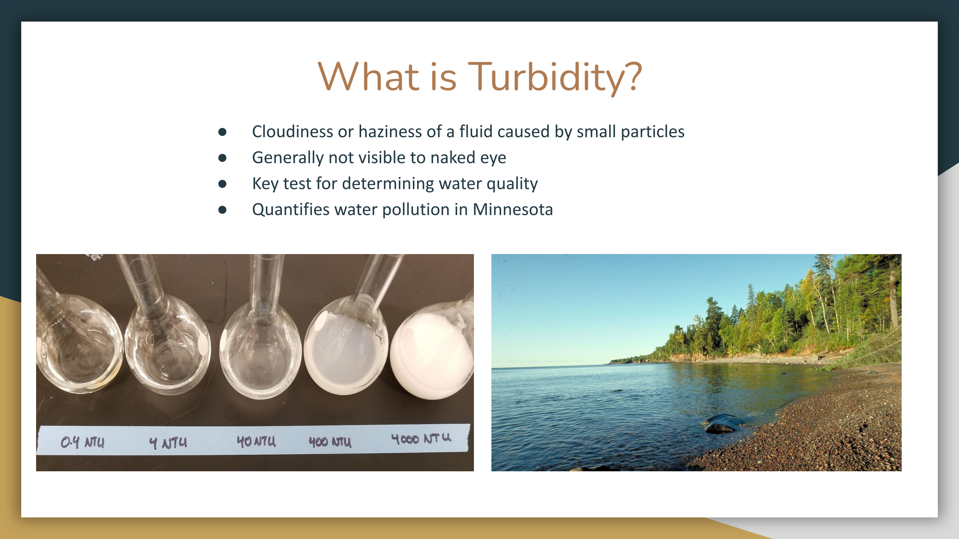
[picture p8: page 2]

- Cloudiness or haziness of a fluid caused by small particles
- Generally not visible to naked eye
- Key test for determining water quality
- Quantifies water pollution in Minnesota

# What is Turbidity?

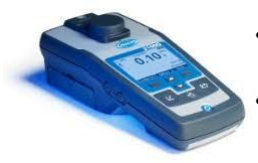
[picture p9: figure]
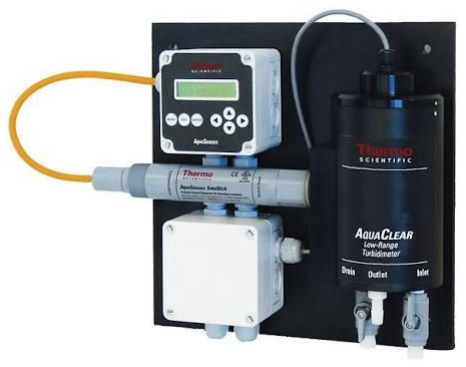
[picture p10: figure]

## - Hach 2100Q Portable Turbidimeter

- $1215

## - Davis Thermo Scientific AquaSensors DataStick AquaClear On-Line Turbidimeter

- $1970

## - Common drinking water standards:

– | WHO Rating: ≤ 5 NTU (ideally ≤ 1 NTU)
– | European Rating: ≤ 4 NTU
– | US Rating: ≤ 1 NTU (ideally ≤ 0.3 NTU)

## - Existing Sensors:

# Project Proposal

## - Develop a functional, low-cost turbidity meter - Uses light scattering to determine the turbidity - Specifications:

- Communicates with an open-source data logger
- Arduino-based code
- Integrate software libraries
■ | ALog
■ | Mayfly
- Low power for prolonged deployment, up to 3 months
- Must be waterproof, submersible up to 3 meters
- Cost less than $100 to produce

## - Field deployable by April

# Team Organization

## - Amanda - Team Lead, Housing, Waterproofing

## - Corbin - Sensor Code, Circuit Design

## - Aaron - Communications, Data Logger Interfacing

## - Erik - Hardware Layout, Mounting, 3D modeling

## - Sean - Housing, Cabling, Waterproofing

## - Jake - Waterproofing, Optics/Hardware Integration

# Measurement Process

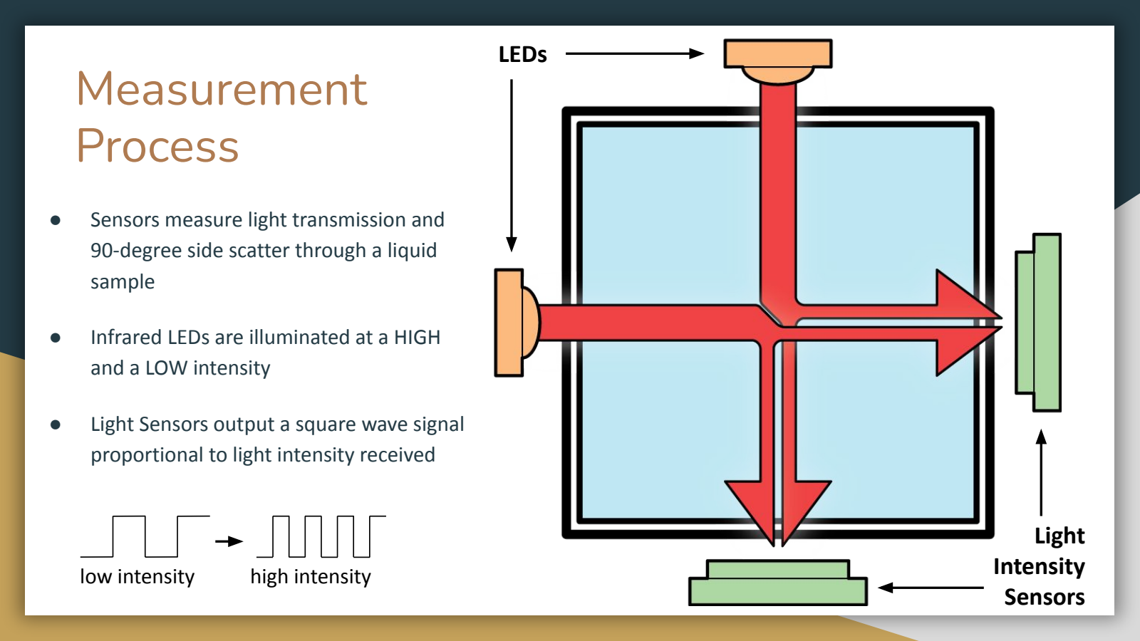
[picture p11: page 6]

Light
Intensity
Sensors
- Sensors measure light transmission and 90-degree side scatter through a liquid sample
- Infrared LEDs are illuminated at a HIGH and a LOW intensity
- Light Sensors output a square wave signal proportional to light intensity received

low intensity high intensity

LEDs

# Measurement Process

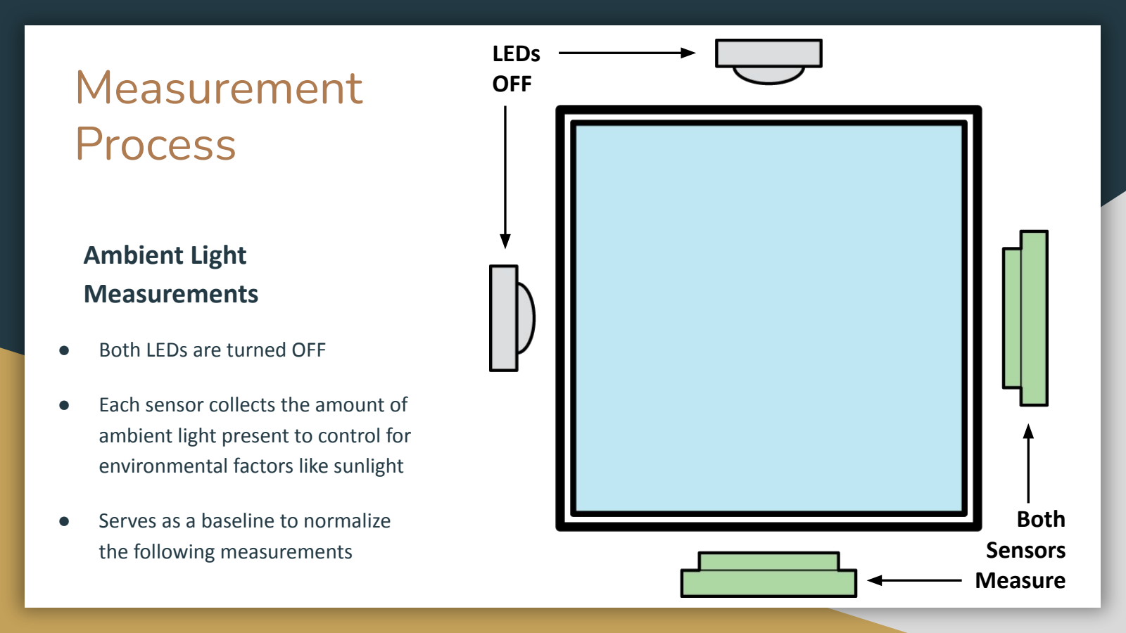
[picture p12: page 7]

Both
Sensors
Measure
- Both LEDs are turned OFF
- Each sensor collects the amount of ambient light present to control for environmental factors like sunlight
- Serves as a baseline to normalize the following measurements

LEDs
OFF

## Ambient Light Measurements

# Measurement Process

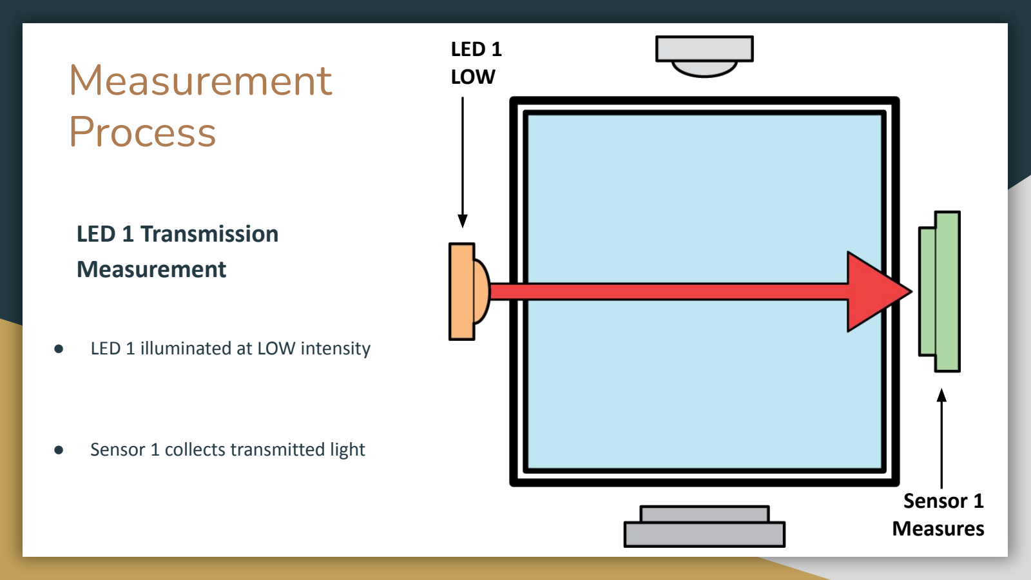
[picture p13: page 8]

Sensor 1
Measures
- LED 1 illuminated at LOW intensity
- Sensor 1 collects transmitted light

LED 1
LOW

## LED 1 Transmission Measurement

# Measurement Process

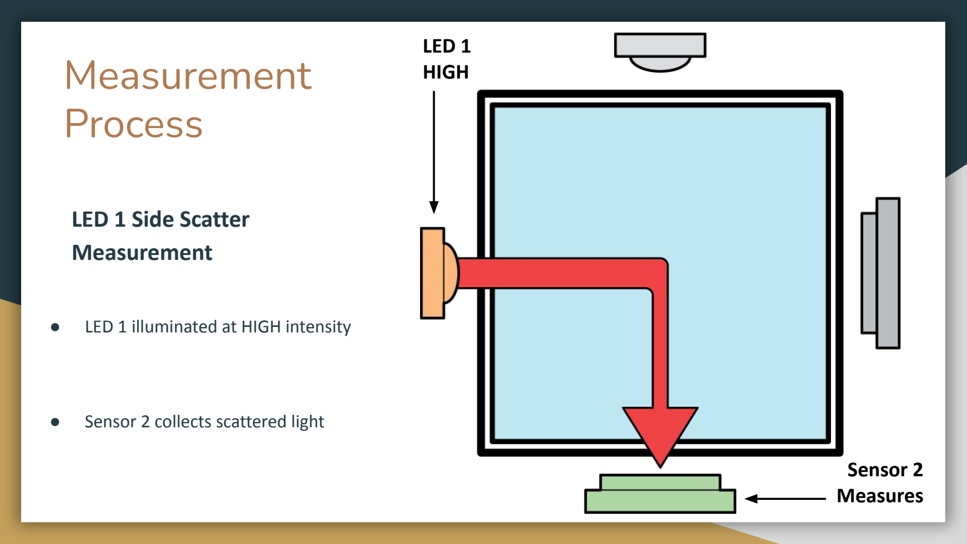
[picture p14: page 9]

Sensor 2
Measures

LED 1
HIGH

## LED 1 Side Scatter Measurement

- LED 1 illuminated at HIGH intensity
- Sensor 2 collects scattered light

# Measurement Process

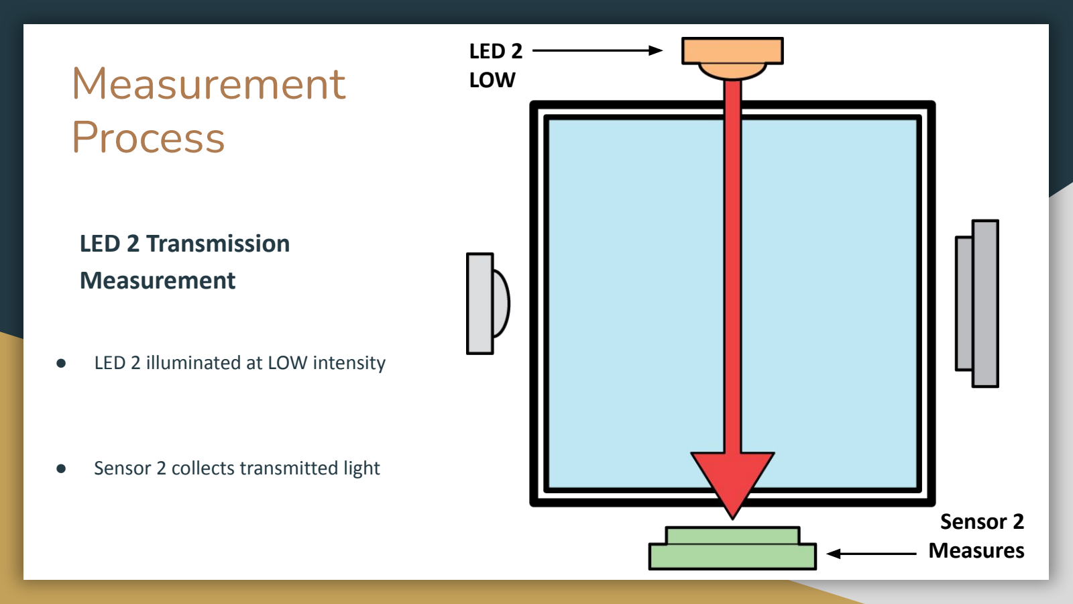
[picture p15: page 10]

Sensor 2
Measures

LED 2
LOW

## LED 2 Transmission Measurement

- LED 2 illuminated at LOW intensity
- Sensor 2 collects transmitted light

# Measurement Process

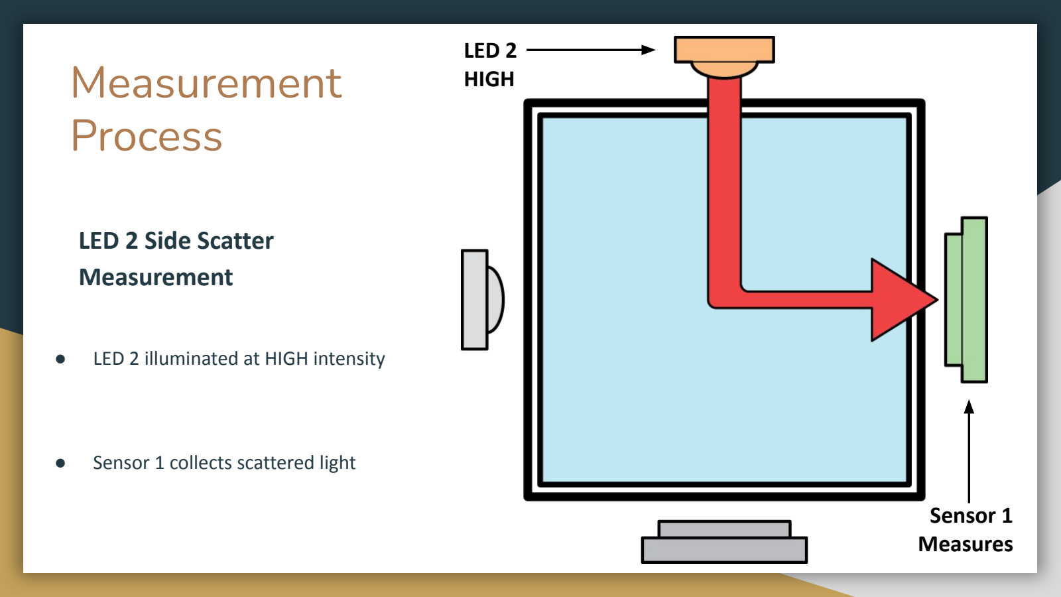
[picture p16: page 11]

Sensor 1
Measures

LED 2
HIGH

## LED 2 Side Scatter Measurement

- LED 2 illuminated at HIGH intensity
- Sensor 1 collects scattered light

# More on Measurement Process

- Measurement routine is repeated five times
- ATmega328P microcontroller collects frequency output by counting rising edges
- Microcontroller averages the five samples of the six measurements
- Measurements are held until the data logger requests them
- Conversion to NTU and long term storage is handled by the data logger

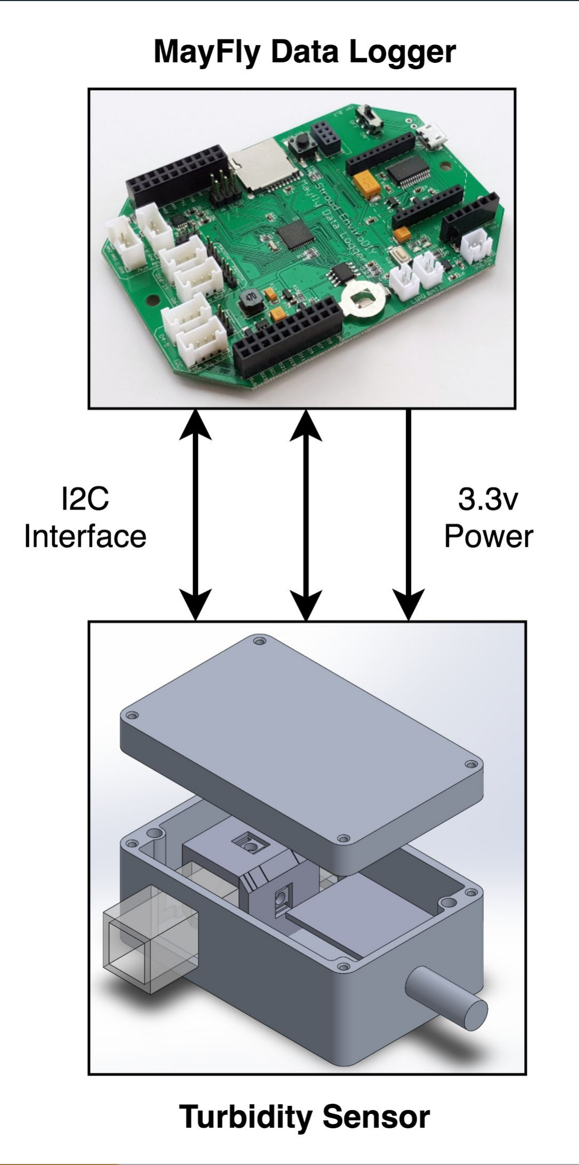
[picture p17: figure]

# Communications

- Goal: A turbidity sensor that can communicate with the MayFly and ALog data loggers.
- Communications Process
- Datalogger (master) requests data from sensor (slave) over I2C interface
- Sensor sends previous readings
- Data logger sends “UPDATE” command
- Sensor takes new measurements (8 minute process)
- Data logger waits ~10 minutes for next measurement
- End Result?
- Turbidity Sensor Library (ALog & Mayfly compatible)

# Hardware Integration / Layout

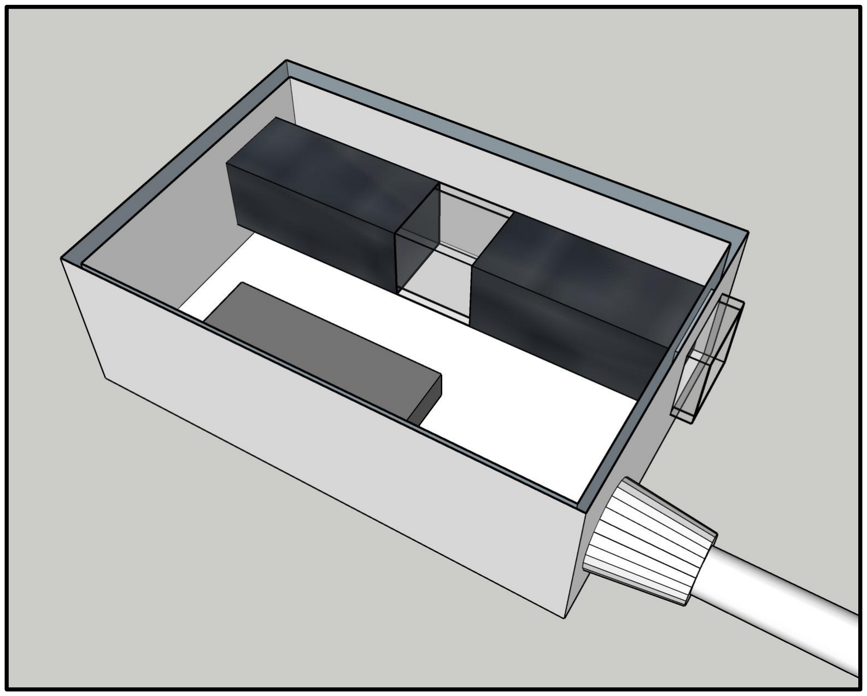
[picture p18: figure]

- Solidworks modeling software (right)
- Horizontal mounting of tube
- Better waterflow

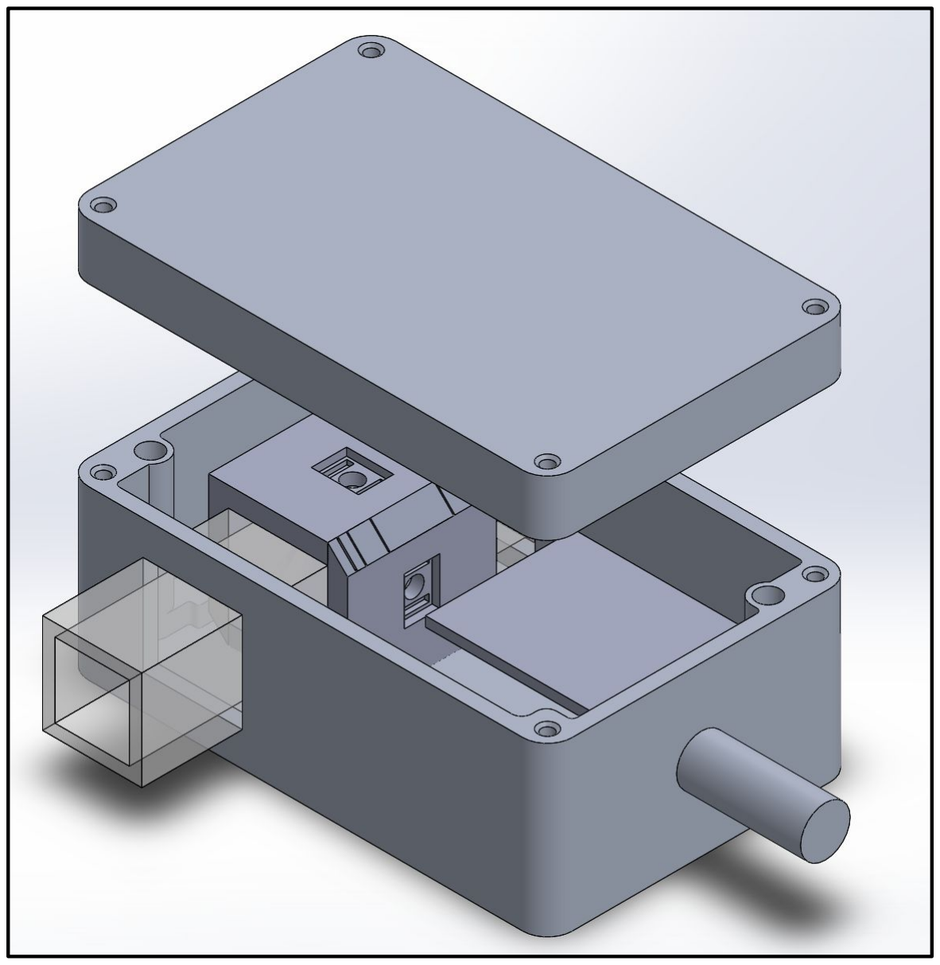
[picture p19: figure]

- Internal circuitry has exact dimensions for fitting
- Enough for perfboard containing all necessary elements
- More space for mounting sensors around tube

# Hardware Integration / Layout

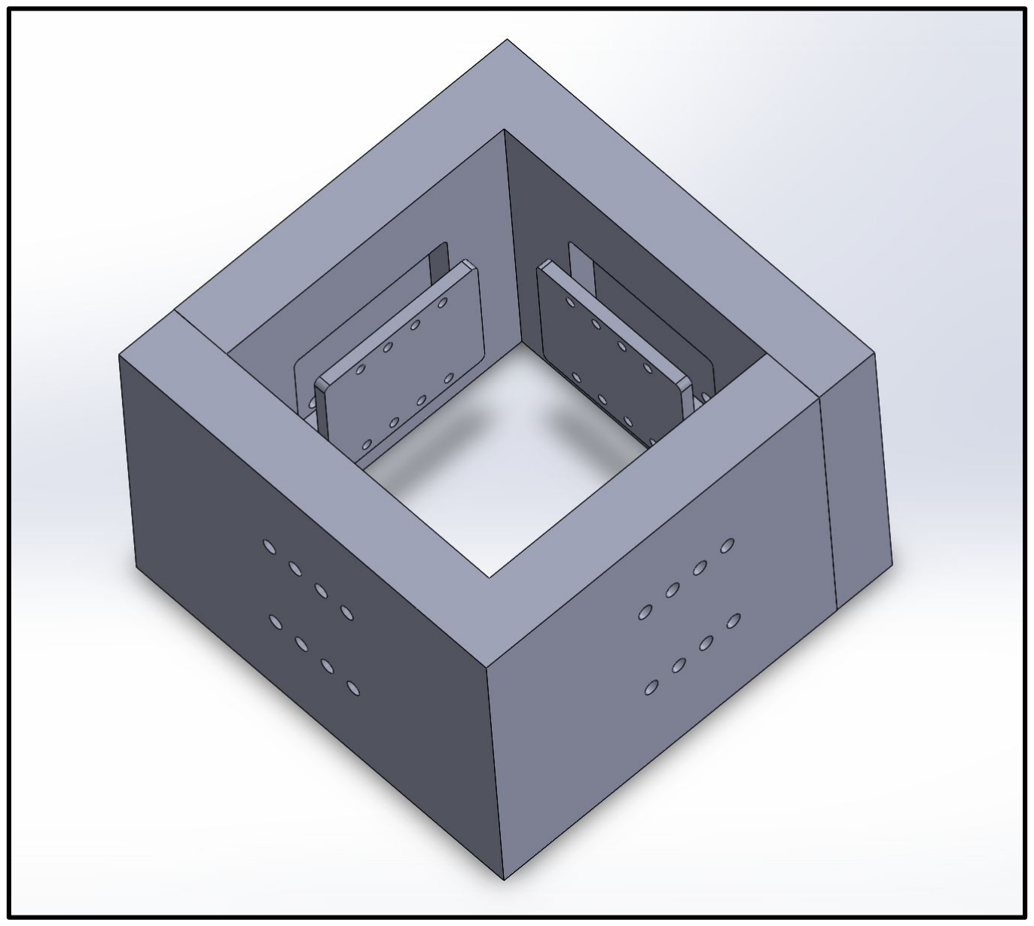
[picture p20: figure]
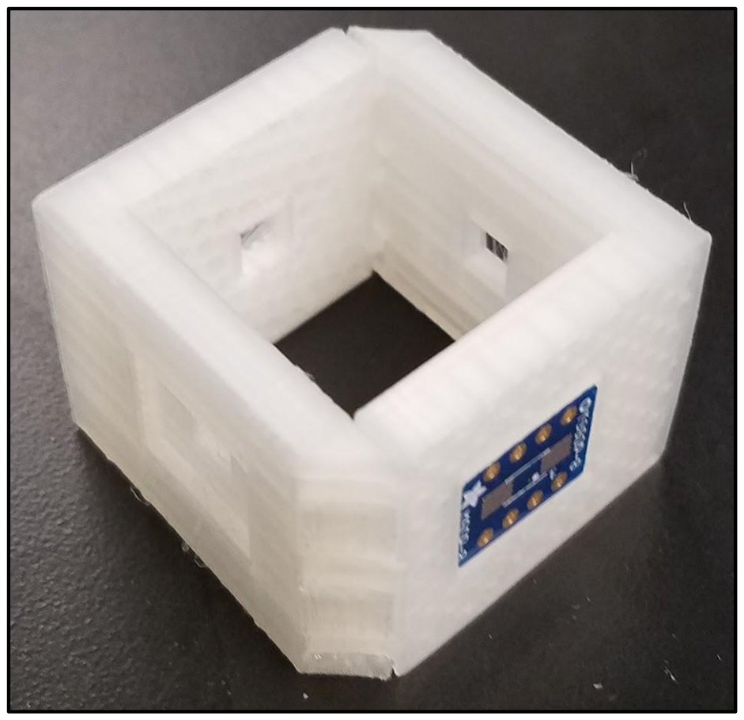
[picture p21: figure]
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

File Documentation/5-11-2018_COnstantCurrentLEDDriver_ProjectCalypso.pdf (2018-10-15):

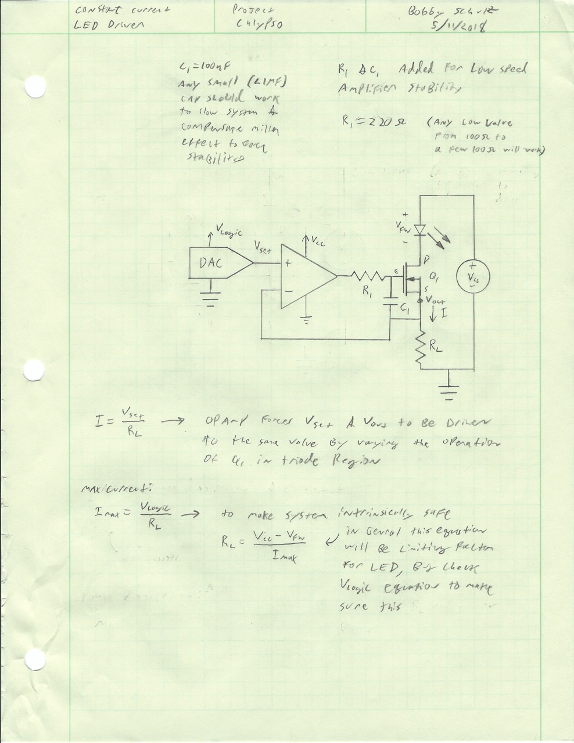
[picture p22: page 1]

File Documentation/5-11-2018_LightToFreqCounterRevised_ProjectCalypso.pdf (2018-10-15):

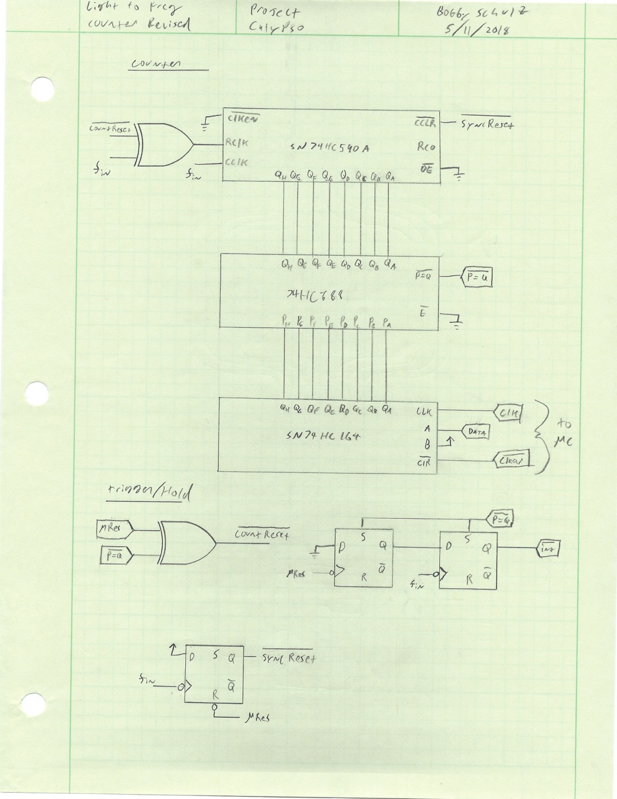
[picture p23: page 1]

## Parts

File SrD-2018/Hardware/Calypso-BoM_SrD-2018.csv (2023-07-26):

Part | Supplier | Supplier Part Number | Manufacturer | Manufacturer Part Number | Quantity | Price (each) | Subtotal | Price (bulk) | Subtotal (100 sensors) | Subtotal (per sensor for 100)
Perfboard (15x20 holes) | Digikey | SBBTH1520-1-ND | Chip Quik Inc. | SBBTH1520-1 | 1 | $3.69 | $3.69 | $3.69 | $369.00 | $3.69
ATmega328P-PU Microcontroller | Digikey | ATMEGA328P-PU-ND | Microchip Technology | ATMEGA328P-PU | 1 | $2.20 | $2.20 | $1.83 | $183.38 | $1.83
28-DIP Socket | Digikey | ED3050-5-ND | On Shore Technology | ED281DT | 1 | $0.33 | $0.33 | $0.22 | $22.05 | $0.22
SN74HC393N Dual Binary Counter | Digikey | 296-8319-5-ND | Texas Instruments | SN74HC393N | 1 | $0.50 | $0.50 | $0.32 | $31.92 | $0.32
14-DIP Socket | Digikey | ED3045-5-ND | On Shore Technology | ED14DT | 1 | $0.18 | $0.18 | $0.12 | $11.96 | $0.12
6-SIP Socket | Digikey | 952-1986-ND | Harwin Inc. | D01-9970642 | 1 | $0.58 | $0.58 | $0.42 | $41.63 | $0.42
8 MHz Crystal | Digikey | 887-1008-ND | TXC Corporation | 9B-8.000MAAJ-B | 1 | $0.39 | $0.39 | $0.26 | $26.00 | $0.26
0.1uF Ceramic Capacitor | Digikey | 399-4329-ND | KEMET | C332C104K5RTA | 3 | $0.22 | $0.66 | $0.09 | $25.50 | $0.26
18 pF Ceramic Capacitor | Digikey | 399-9718-ND | KEMET | C315C180J1G5TA | 2 | $0.43 | $0.86 | $0.18 | $35.64 | $0.36
10 kOhm Resistor | Digikey | RNF18FTD10K0CT-ND | Stackpole Electronics | RNF18FTD10K0 | 1 | $0.10 | $0.10 | $0.03 | $2.75 | $0.03
174 Ohm Resistor | Digikey | 174XBK-ND | Yageo | MFR-25FBF52-174R | 2 | $0.10 | $0.20 | $0.03 | $6.30 | $0.06
976 Ohm Resistor | Digikey | 976XBK-ND | Yageo | MFR-25FBF52-976R | 2 | $0.10 | $0.20 | $0.03 | $6.30 | $0.06
470 Ohm Resistor | Digikey | RNF14FTD470RCT-ND | Stackpole Electronics | RNF14FTD470R | 2 | $0.10 | $0.20 | $0.03 | $5.50 | $0.06
2N7000 N-Channel MOSFET | Digikey | 2N7000TACT-ND | ON Semiconductor | 2N7000TA | 2 | $0.49 | $0.98 | $0.21 | $41.44 | $0.41
860nm IR Emitter | Digikey | 475-3043-1-ND | OSRAM Opto Semiconductors | SFH 4059-QS | 2 | $0.88 | $1.76 | $0.49 | $98.24 | $0.98
Light to Frequency IC | Digikey | TSL238-TCT-ND | AMS | TSL238T | 2 | $5.56 | $11.12 | $3.03 | $605.38 | $6.05
SOT23 to DIP Adapter | Digikey | 1568-1098-ND | SparkFun Electronics | BOB-00717 | 4 | $0.95 | $3.80 | $0.95 | $380.00 | $3.80
3-D Printed Part |  | TBD |  |  |  |  | $0.00 |  | $0.00 | $0.00
Internal Wires |  | TBD |  |  |  |  | $0.00 |  | $0.00 | $0.00
Plug - Female Panel Mount | Digikey | SC266-ND | Switchcraft Inc. | EN3P6FX | 1 | $10.87 | $10.87 | $7.22 | $722.00 | $7.22
Plug - Male Cable Mount | Digikey | SC258-ND | Switchcraft Inc. | EN3C6MX | 1 | $8.48 | $8.48 | $5.74 | $574.00 | $5.74
Cable | Digikey | T1346-5-ND | Tensility International Corp | 30-00507 | 1 | $13.03 | $13.03 | $10.65 | $1,065.00 | $10.65 | could be purchased at longer lengths and cut to desired size
Enclosure | Polycase | AN-14P | Polycase | AN-14P | 1 | $15.40 | $15.40 | $10.30 | $1,030.00 | $10.30
Inlet Tube | ePlastics | ACREXST1.000 | ePlastics | ACREXST1.000 (6 ft lengths) | 1 | $13.53 | $13.53 | $10.50 | $94.50 | $0.95 | need 9 lengths
Total |  |  |  |  |  |  | $89.06 |  | $5,378.49 | $53.78
Consumables
Spray Paint | Menards | 5578090 | Rust-Oleum | Flat Protective Enamel Paint | 1 | $3.96 | $3.96
Caulk | Menards | 5202628 | Loctite | PL Marine Adhesive Sealant | 1 | $12.97 | $12.97
Total |  |  |  |  |  |  | $16.93

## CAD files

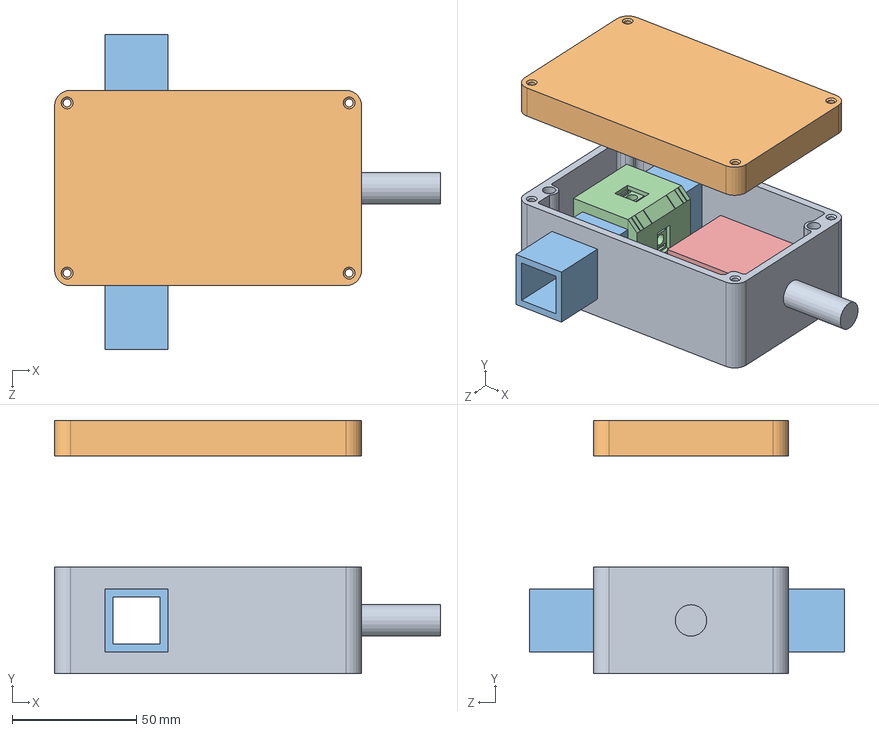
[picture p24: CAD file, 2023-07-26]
SrD-2018/Hardware/Metal Box Assembly.SLDASM
155.6 x 102.0 x 127.0 mm
Metal Box
Metal Box Top
Tube
3D Printed Part_notched_FINAL x 2
PCB

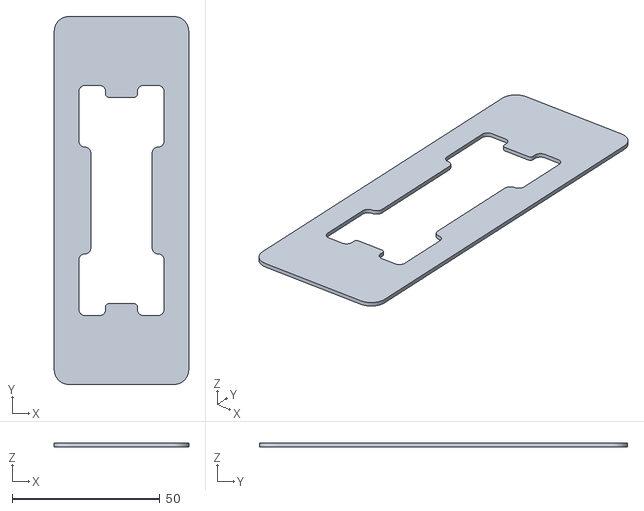
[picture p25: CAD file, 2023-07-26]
3Dprint/StencilMount_Calypso.STL
45.5 x 124.4 x 1.20

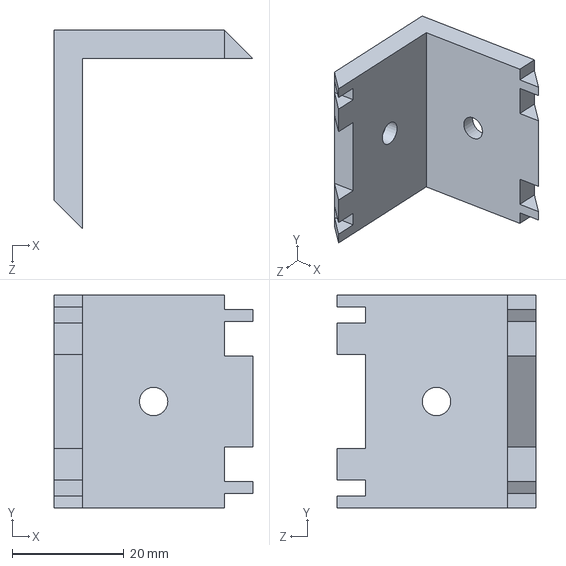
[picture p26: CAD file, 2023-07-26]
SrD-2018/Hardware/3D Printed Part_notched_FINAL.SLDPRT
35.6 x 38.1 x 35.6 mm

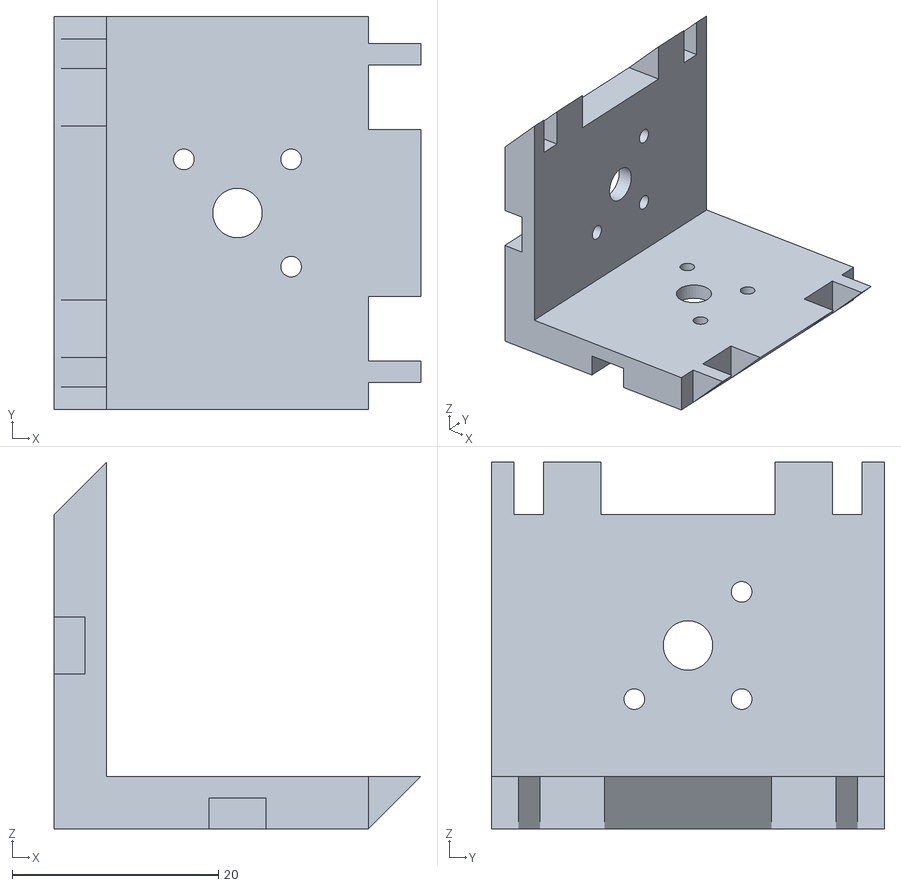
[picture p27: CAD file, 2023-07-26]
3Dprint/Calypso_OpticsMount_v2.STL
35.6 x 38.1 x 35.6

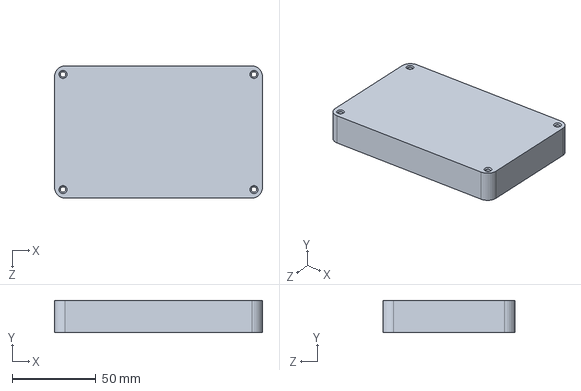
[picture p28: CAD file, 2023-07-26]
SrD-2018/Hardware/Metal Box Top.SLDPRT
123.8 x 19.1 x 78.7 mm

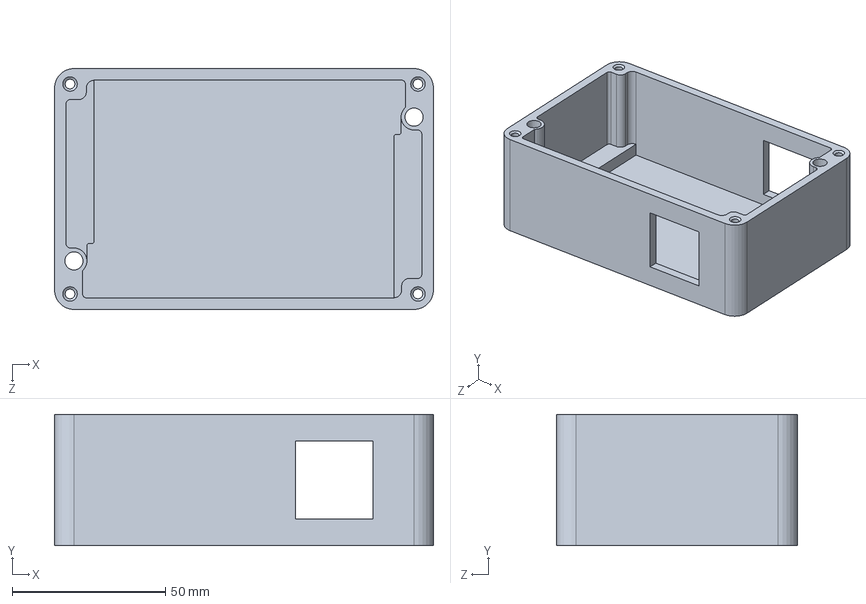
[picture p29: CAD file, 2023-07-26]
SrD-2018/Hardware/Metal Box.SLDPRT
123.8 x 42.9 x 78.7 mm

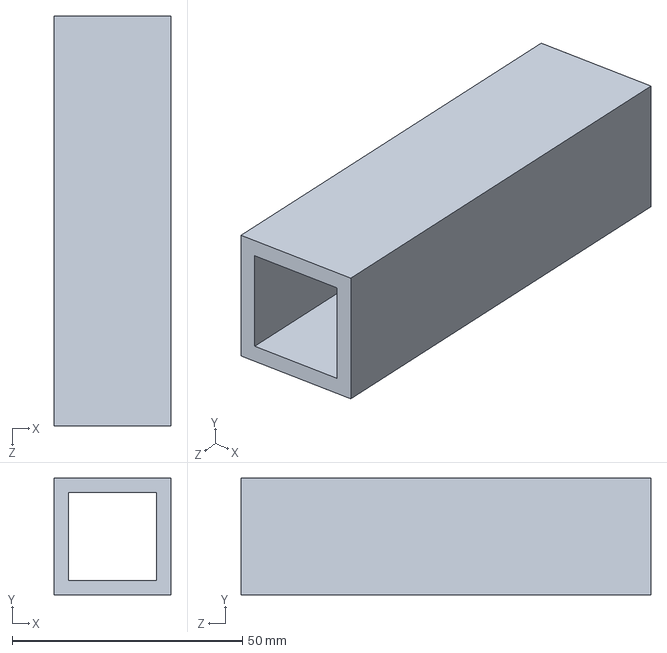
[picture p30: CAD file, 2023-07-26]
SrD-2018/Hardware/Tube.SLDPRT
25.4 x 25.4 x 88.9 mm

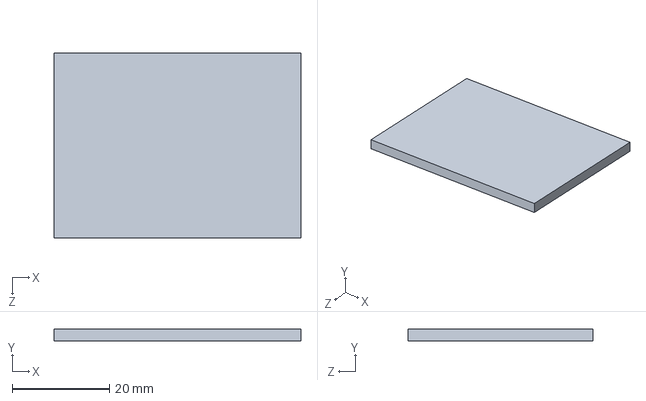
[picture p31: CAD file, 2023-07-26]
SrD-2018/Hardware/PCB (not real one).SLDPRT
50.8 x 2.54 x 38.1 mm

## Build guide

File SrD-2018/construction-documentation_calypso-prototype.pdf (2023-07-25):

Turbidity Sensor Construction Documentation University of Minnesota
EE 4951W

Group Members:
Corbin Buechler
Amanda Hayden
Aaron Nightingale
Sean Rogers
Erik Sundberg
Jacob Wolf

Table of Contents

1. Assembly Instructions
a. Enclosure
i. Cutouts for Inlet Tube and Plug
ii. | Plug Wiring and Installation
iii. | Inlet Tube Installation and Waterproofing
b. Cabling
c. Circuitry
2. Programming Instructions
a. Programming a New ATmega328P Chip
b. Programming the ATmega328P in the Sensor

Enclosure Assembly

Parts Required:
- Polycase AN-14P Aluminum Box Tools Required:
- Dremel or other small metal cutting saw
- Power drill or drill press
- Vice
- Ruler
- Pencil
- Phillips Screwdriver
- Compressed air
- Silicone Caulk
- Black spray paint

Cutouts for Inlet Tube and Plug
1. Remove the lid and gasket from the assembly and set aside. They are not altered during the construction.
2. The short edges are sides A and B. The long edges are sides C and D. The bottom side is side E
3. Side A will be for the plug. The center of the plug hole will be ⅞” from the edge of side E and 1.5” from sides C and D.
4. Using power drill or drill press, cut a hole in the enclosure just large enough to fit the plug.
5. Test to make sure the plug fits snugly in the drilled hole. Re-drill hole with slightly bigger bit until plug fits snugly.
6. The square cutouts for the tubes will be on sides C and D, next to side B. The squares are 1-1/16” on each side. The cutout should be 0.5” from the edge of side B and ⅜” from the bottom side E. The cutout should be a little higher than midline to account for space needed during instrument installation.
7. Using a Dremel or other small saw, cut along the lines on both sides, measured in the previous step. Make sure to limit overshooting the lines to avoid needing to use more silicone caulk when sealing the enclosure.
8. File down any rough corners and edges to create as smooth an edge as possible.
9. Test fit by sliding tube through both square holes. Repeat steps 7 and 8 until tube can slide tightly through both cutouts.
10.Using compressed air, clean out any metal shavings from cutouts and enclosure.
11. The final enclosure should look similar to the following pictures.

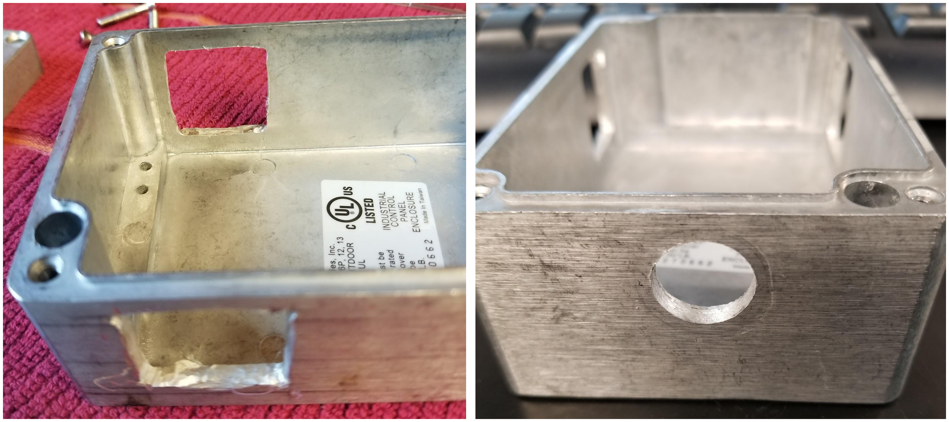
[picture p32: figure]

Pictures for Cutouts Step 11.

Plug Wiring and Installation
1. Following the steps in the cable assembly section, solder the wires to be connected to the circuit to the male end of the plug in the same orientation as was followed in the cable assembly.
2. With the hole drilled so that plug fits snugly, insert the plug into the hole so that the female end is out of the enclosure and the soldered wires into the enclosure.
3. While holding the plug in place, apply a small amount of silicone all around the outside of the plug against the enclosure (although the plug makes its own seal, this is for added protection).
4. Install the hex nut that holds the plug in place. It will compress the silicone that was applied creating a watertight seal.

Inlet Tube Installation
1. Put a piece of tape (approx .75 in width) all the way around in the lengthwise center of the tube, this will be the LED and sensor area that is not to be painted.
2. Using the black spray paint, paint the entire surface of the acrylic tube so that no ambient light is able to enter the tube through the acrylic.
3. Tape around the inside of the newly cut square opening in the enclosure to avoid scratching the acrylic tube.
4. Put the acrylic tube through the holes cut into the enclosure centering it on the enclosure.
5. Tape to hold in place while applying the waterproofing.
6. Tape off areas on both the acrylic tube and outside of the enclosure to avoid getting the silicone in areas where it is undesired.
7. Apply silicone to both the inside and outside of the enclosure on all sides of the acrylic tube to completely protect from water intrusion

Cable Assembly

Parts Required
- Switchcraft Male Cable Mount Plug Assembly
- Tensility PVC Cable
- Silicone Caulk
Tools Required
- Wire stripper and cutter
- Soldering iron
- Multimeter or continuity tester

Steps
1. Strip a maximum of 0.625” (0.500” should be more than adequate) of outer insulation from one end of the PVC cable.
2. Strip a maximum of of 0.218” from each conductor within the cable.
3. Tin the exposed end of each conductor with the soldering iron.
4. Open the product datasheet (http://www.switchcraft.com/Drawings/en3c_m_c_cd.pdf) and follow the instructions for proper assembly of plug components onto the cable. They can be found on page 2 of the document. If you cannot click the link, open the “Switchcraft Cable Mount Male Plug Drawing.pdf” file in the “Data Sheets folder”.
5. Make sure all plug assembly pieces are far enough away from the end so they do not interfere with soldering.
6. Next, following the below color scheme, solder each conductor into the specified connector. See page 1 of the datasheet for the 6-conductor orientation and number scheme.
a. 1 - black (GND)
b. 2 - red (+3.3V)
c. 3 - green (BUSY)
d. 4 - yellow (SCL)
e. 5 - blue (SDA)
f. 6 - white (UNUSED PIN)
7. Using a multimeter or continuity tester, test for continuity between the solder joint and front of the plug.

Circuitry

The turbidity sensor schematic is shown on the following page, with the abbreviated Bill of Materials below to serve as a key to identify the individual parts in the schematic. For our build, this circuit fit on a 15 by 20 hole perfboard with little extra room. Since it is assumed that a production version of the turbidity sensor would use a custom printed circuit board, the perfboard layout is not described in detail in this documentation.

As is mentioned in the accompanying Project Design Notes documents (Calibration section), the design as shown here produced some saturation/non-linear behavior from the light sensors, which limited the amount of data that could be fit for conversion to NTU. If the MOSFET and fixed resistor scheme was attempted again, we would recommend decreasing R6/R7, which would increase the higher LED brightness for side-scatter measurements, and increasing R4/R5 so that R4+R6 and R5+R7 (which determines the lower LED brightness for transmission measurements), is increased. These changes would increase the side-scatter frequencies and decrease the transmission frequencies in low turbidity situations, which should result in useful data collection over a larger range of turbidity.

Bill of Materials

Symbol | Part | Manufacturer | Digi-Key Part Number | Quantity
C1, C2, C3 | 0.1 uF Ceramic Capacitor | KEMET | 399-4329-ND | 3
C4, C5 | 18 pF Ceramic Capacitor | KEMET | 399-9718-ND | 2
Q1, Q2 | 2N7000 N-Channel MOSFET | ON Semiconductor | 2N7000TACT-ND | 2
R1 | 10 kOhm Resistor | Stackpole Electronics | RNF18FTD10K0CT-ND | 1
R2, R3 | 470 Ohm Resistor | Stackpole Electronics | RNF14FTD470RCT-ND | 2
R4, R5 | 976 Ohm Resistor | Yageo | 976XBK-ND | 2
R6, R7 | 174 Ohm Resistor | Yageo | 174XBK-ND | 2
L1, L2 | 860 nm Infrared LED | OSRAM Opto Semi | 475-3043-1-ND | 2
U1 | ATmega328P Microcontroller | Microchip Technology | ATMEGA328P-PU-ND | 1
U2 | SN74HC393N Dual Binary Counter | Texas Instruments | 296-8319-5-ND | 1
U4, U3 | Light Sensor | AMS | TSL238-TCT-ND | 2
X1 | 8 MHz Crystal | TXC Corporation | 887-1008-ND | 1

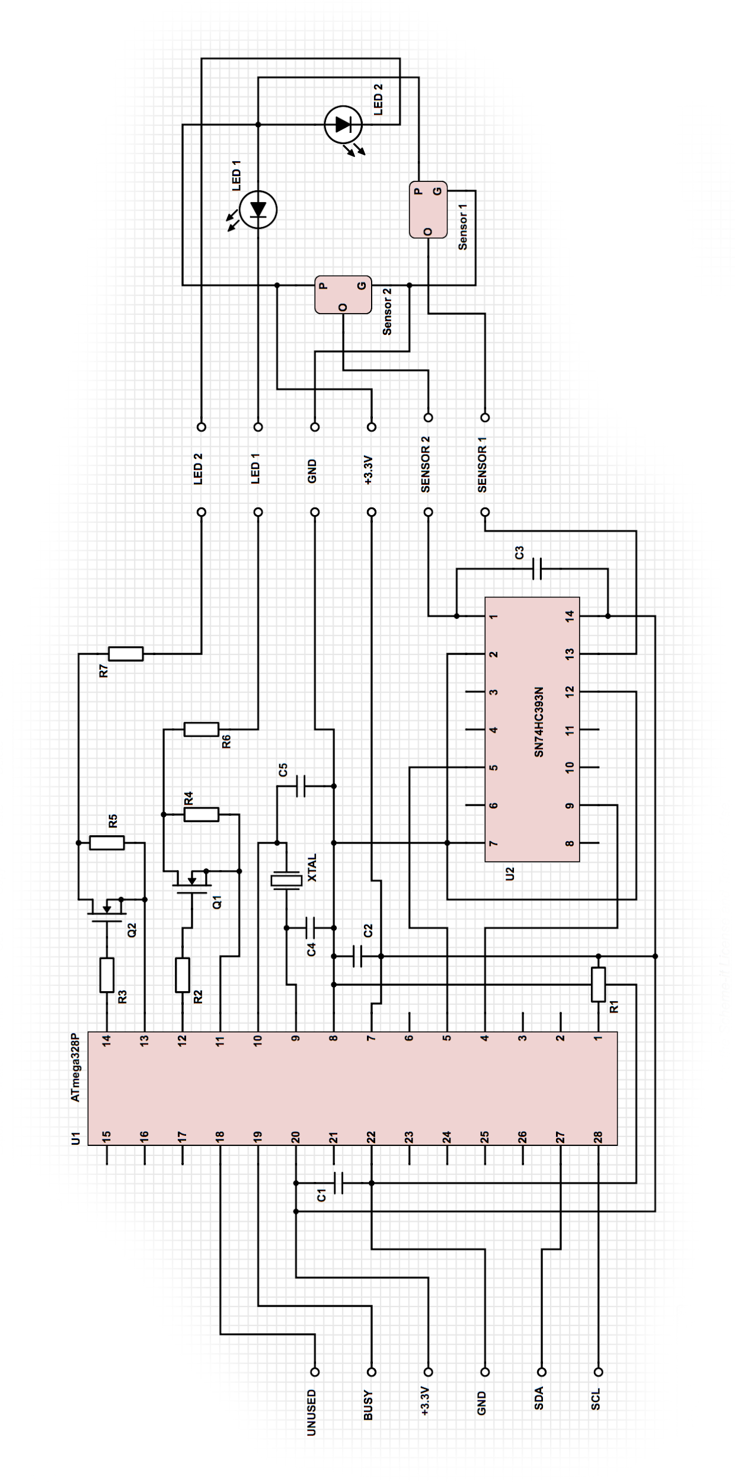
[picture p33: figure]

Programming Instructions

This section will explain how the ATmega328P is programmed to work in a standalone circuit, and how to program it externally without removing it from the sensor’s circuit. Most of this process follows the “From Arduino to a Microcontroller on a Breadboard” (https://www.arduino.cc/en/Tutorial/ArduinoToBreadboard) tutorial with some changes for implementing the 8 MHz external crystal. The images in this section are taken from this tutorial.

Programming a New ATmega328P Chip
The first step is to burn the Arduino bootloader on a new ATmega chip, which requires using an Arduino Uno board as an in-system program (ISP). The step-by-step process is below.
1. Upload the ArduinoISP sketch (one of the
Built-in Example sketches in the Arduino IDE) to the Arduino Uno board.
2. Wire up the circuit shown in the diagram to the right, with a couple changes. Besides the Arduino Uno and the ATmega328P, the other required parts are an 8 MHz crystal, 10 kOhm resistor, and two 18 pF ceramic capacitors. Also, instead of powering the breadboard with 5V, you should use 3.3V.
3. Select “Arduino Pro or Pro Mini” from the Tools > Board menu and “ATmega328P (3.3V, 8MHz)” from the Tools > Processor menu.
4. Select “Arduino as ISP” from Tools > Programmer
5. Run Tools > Burn Bootloader

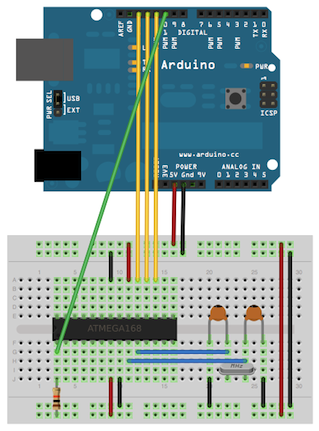
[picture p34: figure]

The ATmega is now ready to be programmed with the sensor code. This can be done using the Arduino Uno board with its microcontroller removed. From this point on, the only connections needed are the ones shown in the diagram below. Again, 3.3V should be used for power instead of 5V. The Board and Processor selections made above should stay the same. From there, any sketch can be uploaded to the ATmega using the usual process.

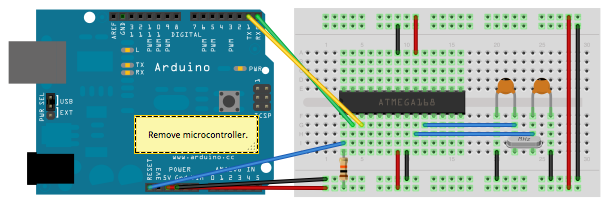
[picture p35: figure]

Programming the ATmega328P in the Sensor
On our sensor’s circuit board, there are five sockets which allow the connections in the diagram above to be made to RESET, 3.3V, GND, TX, and RX on an Arduino Uno board so the chip can be reprogrammed without removing it from the sensor. Note that the diagram uses 5V power, but our circuit needs 3.3V instead. Simply make these connections to an Uno (with the microcontroller removed), and upload to the ATmega using the usual process.

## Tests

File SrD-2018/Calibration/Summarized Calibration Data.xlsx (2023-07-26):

Turbidity (NTU) | Sample | L1 Transmission (Hz) | L1 Scatter (Hz) | L2 Transmission (Hz) | L2 Scatter (Hz)
0.0004 | 1 | 552317.53 | 4139.76 | 361995.76 | 6421.53
0.0004 | 2 | 552445.73 | 4148.47 | 362268.47 | 6429.73
0.0004 | 3 | 553037.87 | 4148.94 | 362716.94 | 6429.87
0.0004 | 4 | 553614.07 | 4149.33 | 363157.33 | 6430.07
0.0004 | 5 | 554022.13 | 4149.80 | 363445.80 | 6446.13
0.0004 | 6 | 553940 | 4160.00 | 363424.00 | 6444.00
0.0004 | 7 | 553696 | 4152.00 | 363304.00 | 6440.00
0.0004 | 8 | 553512 | 4148.00 | 363180.00 | 6440.00
0.0004 | 9 | 553344 | 4156.00 | 363084.00 | 6432.00
0.0004 | 10 | 553172 | 4144.00 | 362960.00 | 6428.00
0.4 | 1 | 542856.00 | 4699.47 | 360363.47 | 6792.00
0.4 | 2 | 542864.00 | 4723.00 | 360147.00 | 6816.00
0.4 | 3 | 542544.00 | 4738.46 | 361082.46 | 6832.00
0.4 | 4 | 542023.60 | 4769.93 | 361513.93 | 6855.60
0.4 | 5 | 541711.40 | 4769.66 | 361977.66 | 6863.40
0.4 | 6 | 541864.00 | 4808.00 | 362312.00 | 6904.00
0.4 | 7 | 542048.00 | 4864.00 | 361944.00 | 7048.00
0.4 | 8 | 541944.00 | 4816.00 | 361728.00 | 6960.00
0.4 | 9 | 541544.00 | 4760.00 | 361616.00 | 6776.00
0.4 | 10 | 541408.00 | 4848.00 | 361832.00 | 6832.00
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

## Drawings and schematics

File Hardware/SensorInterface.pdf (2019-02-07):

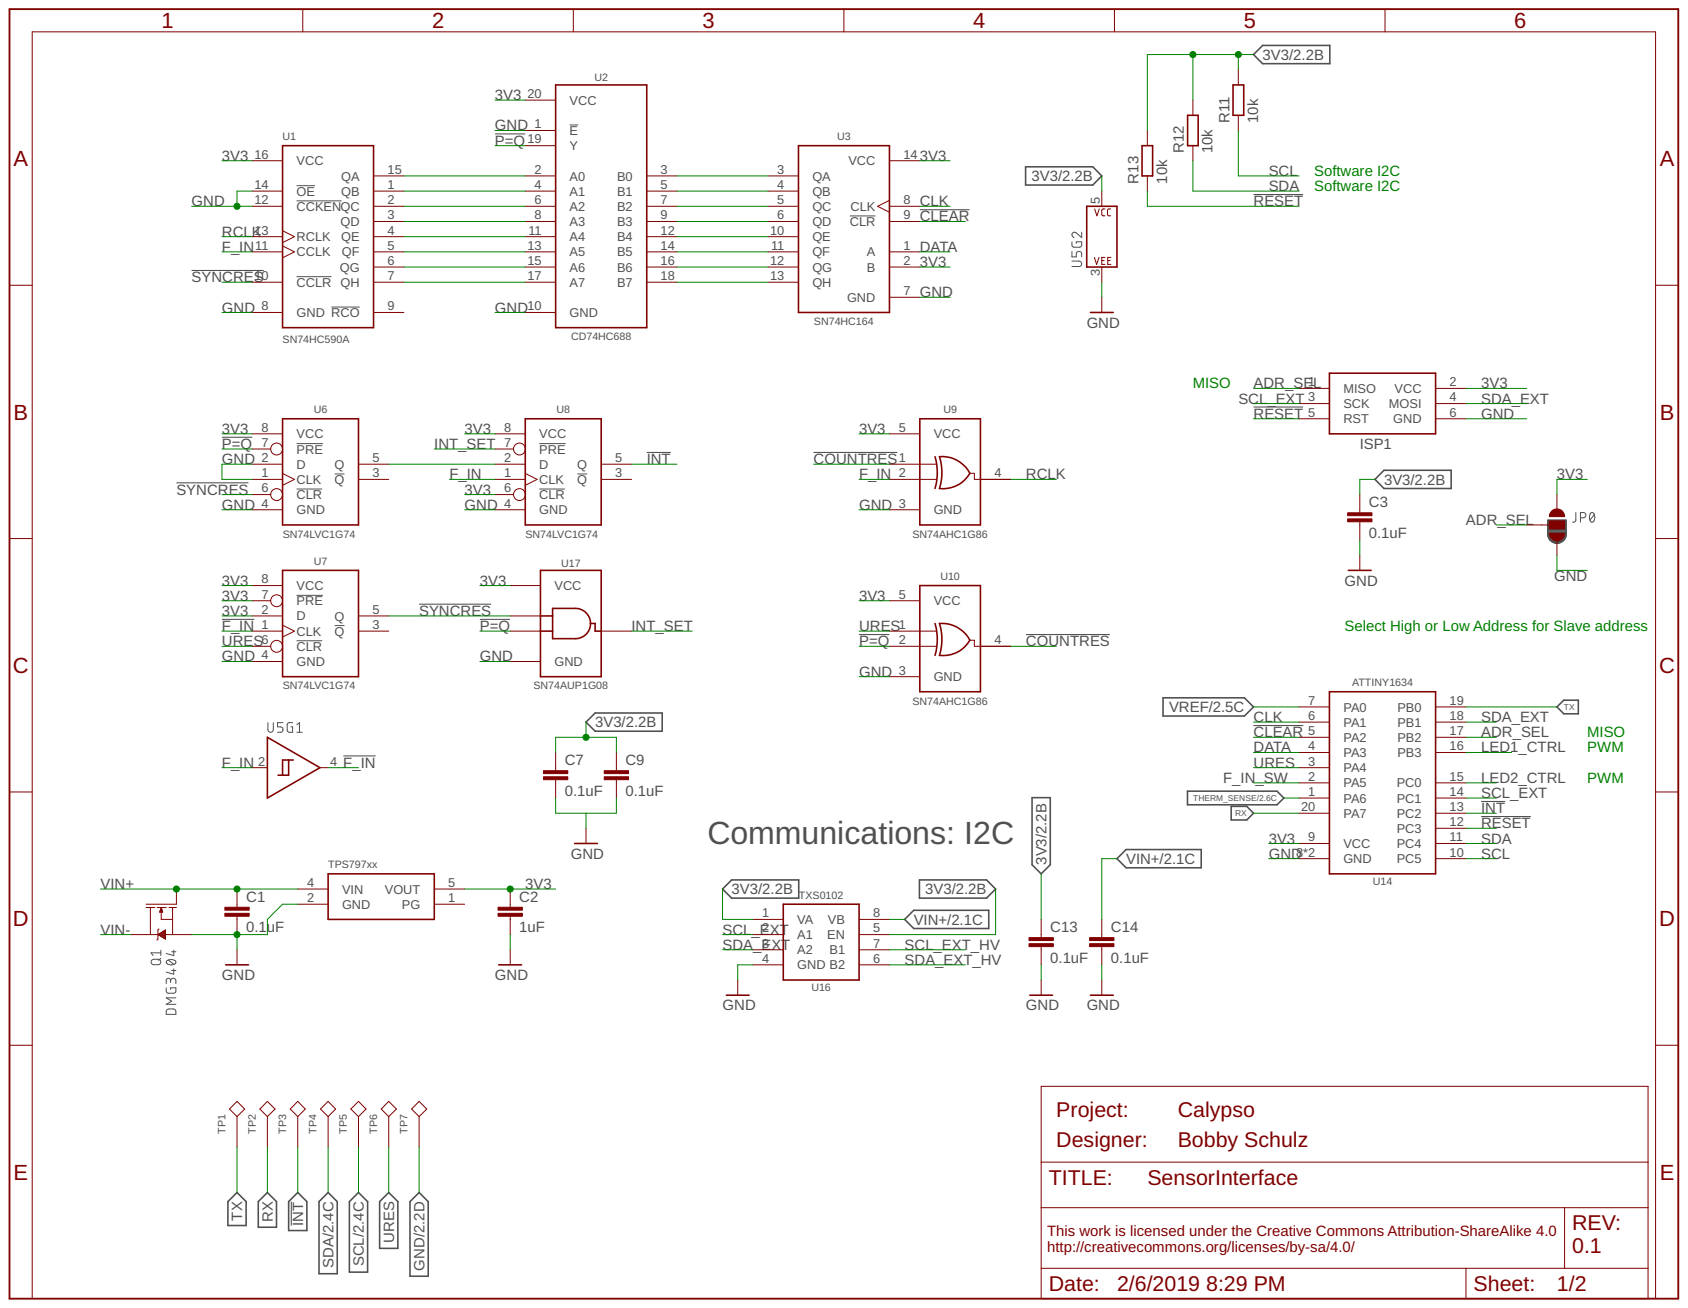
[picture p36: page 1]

Select High or Low Address for Slave address PWM

This work is licensed under the Creative Commons Attribution-ShareAlike 4.0 http://creativecommons.org/licenses/by-sa/4.0/ | REV: 0.1

Date: 2/6/2019 8:29 PM | Sheet: 1/2

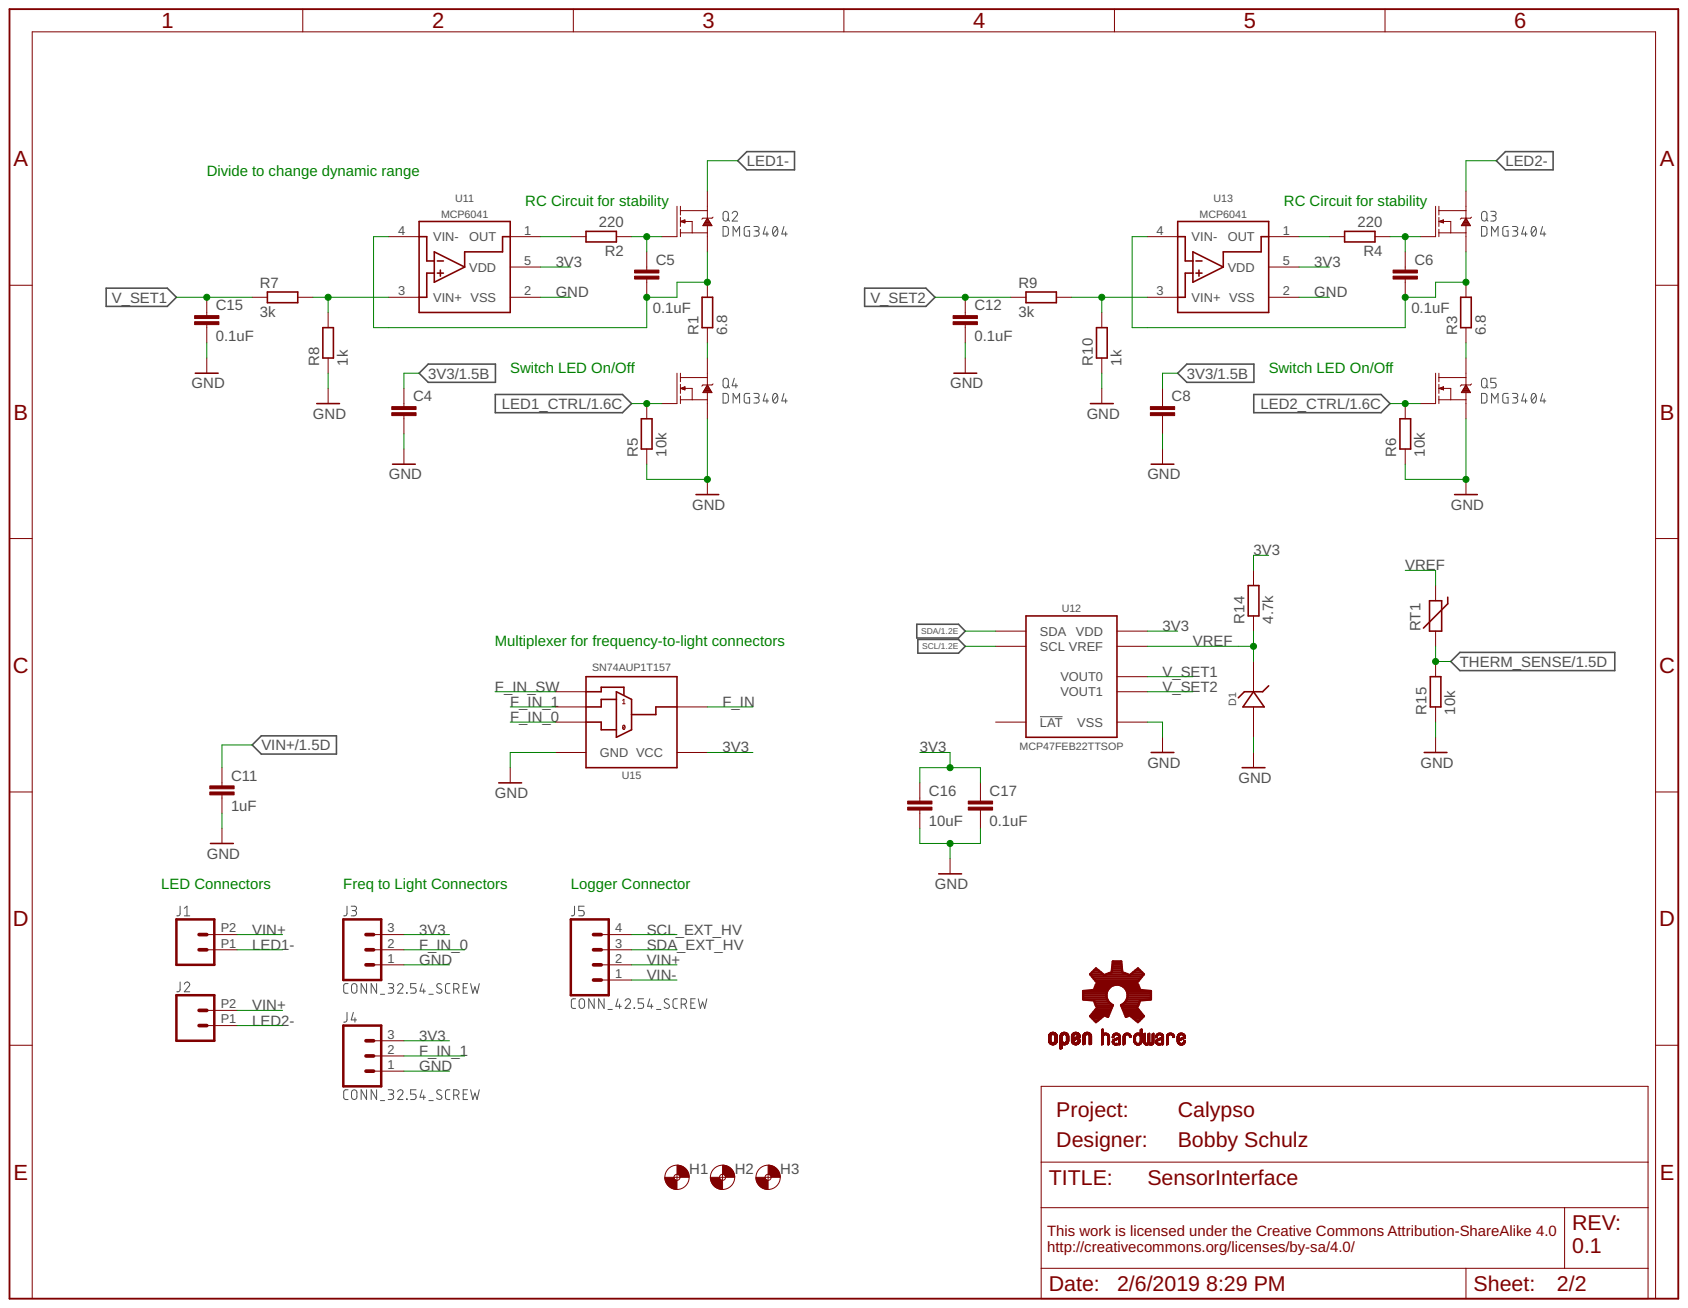
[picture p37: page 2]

Divide to change dynamic range

Multiplexer for frequency-to-light connectors

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

Date: 2/6/2019 8:29 PM | Sheet: 2/2

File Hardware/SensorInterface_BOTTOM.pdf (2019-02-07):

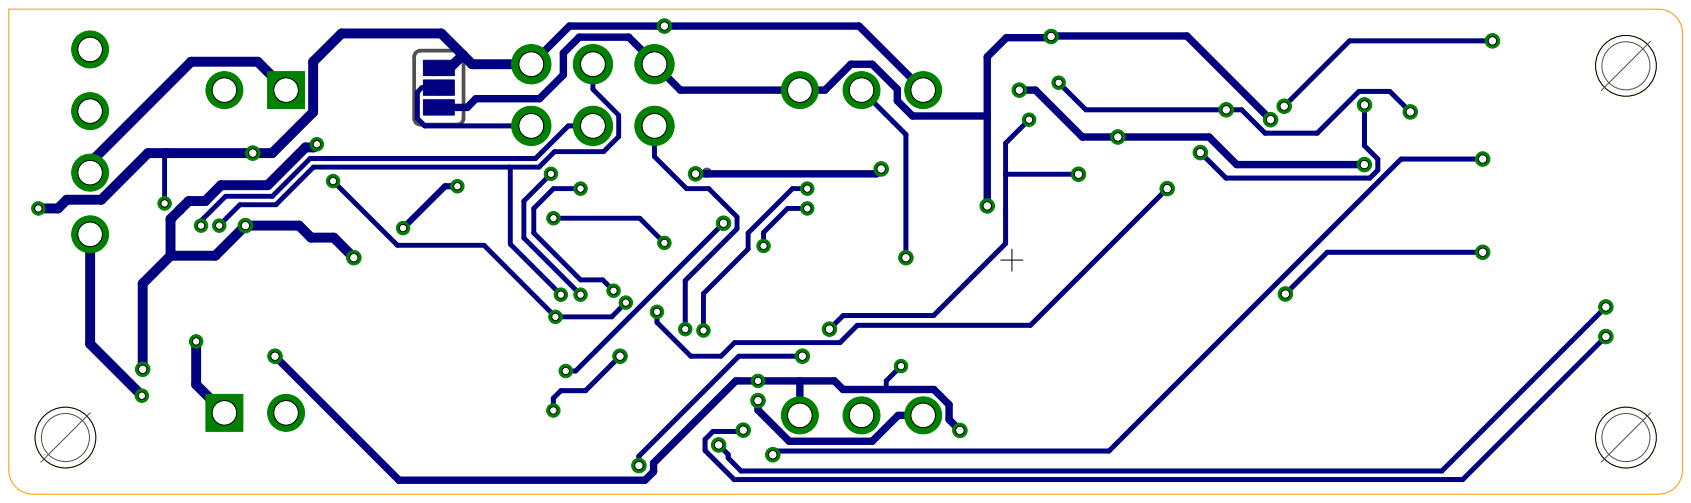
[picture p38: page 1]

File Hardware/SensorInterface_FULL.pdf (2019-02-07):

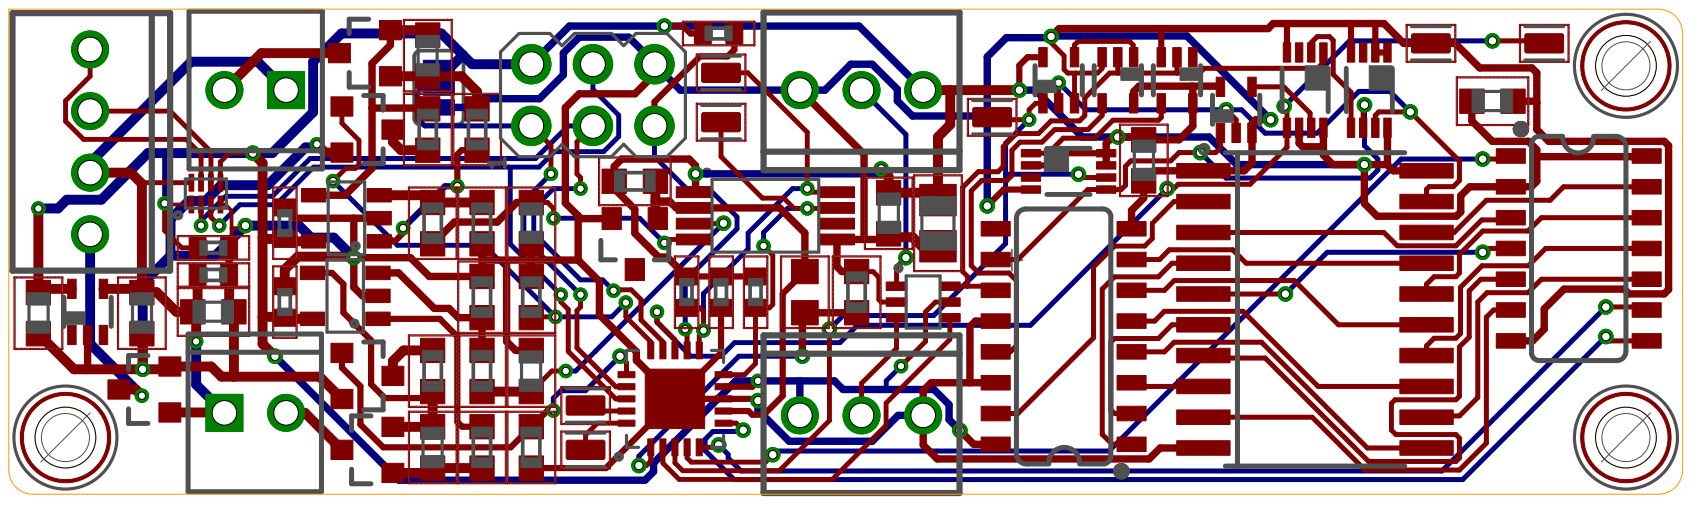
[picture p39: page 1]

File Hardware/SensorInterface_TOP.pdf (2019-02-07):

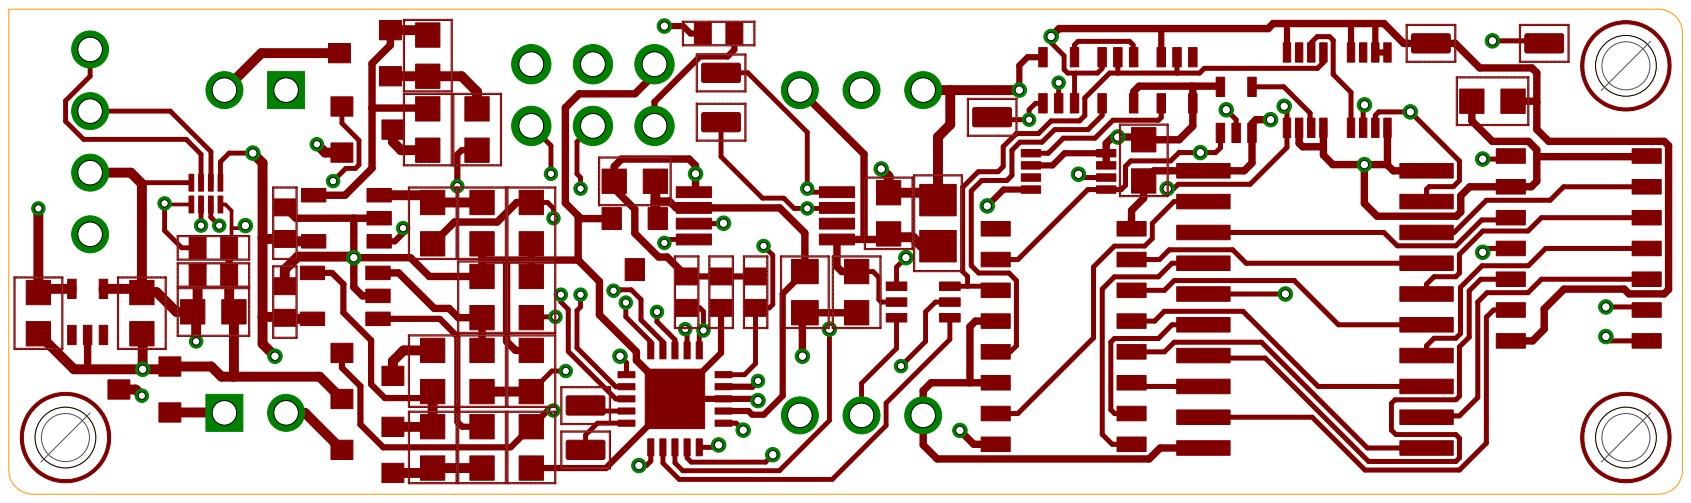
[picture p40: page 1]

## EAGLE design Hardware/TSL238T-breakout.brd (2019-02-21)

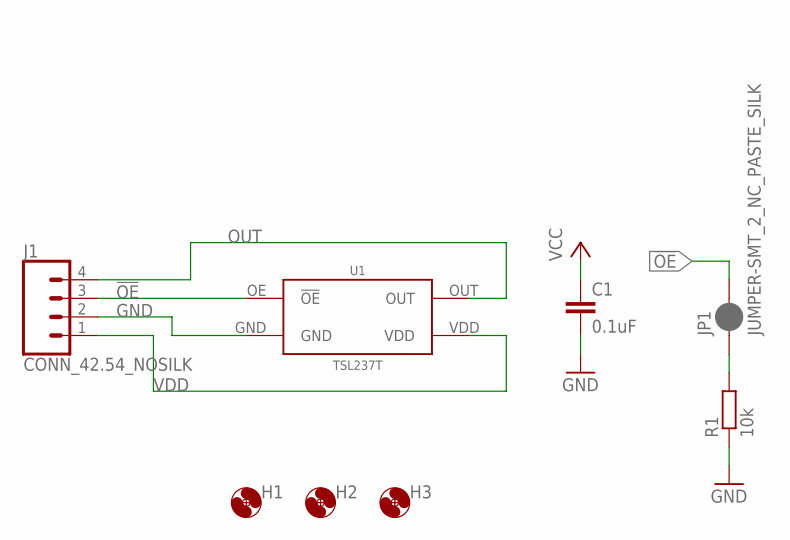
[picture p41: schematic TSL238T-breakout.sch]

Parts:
C1: 0.1uF; C0402
H1, H2, H3: MOUNTING_HOLE2_NP; 2_56
J1: CONN_42.54_NOSILK; 1X04_NOSILK
JP1: JUMPER-SMT_2_NC_PASTE_SILK; SMT-JUMPER_2_NC_PASTE_SILK
R1: 10k; R0402
U1: TSL237T

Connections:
!OE: J1.3, JP1.2, U1.OE (!OE)
GND: C1.2, J1.2, R1.1, U1.GND
unnamed: JP1.1, R1.2
OUT: J1.4, U1.OUT
VDD: C1.1, J1.1, U1.VDD

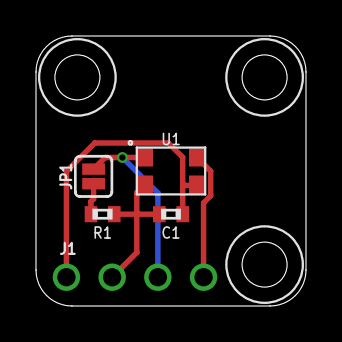
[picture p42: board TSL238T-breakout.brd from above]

Board: 2 copper layers, 15.0 x 15.0 mm, 8 parts (0 on the bottom side), 5 nets.

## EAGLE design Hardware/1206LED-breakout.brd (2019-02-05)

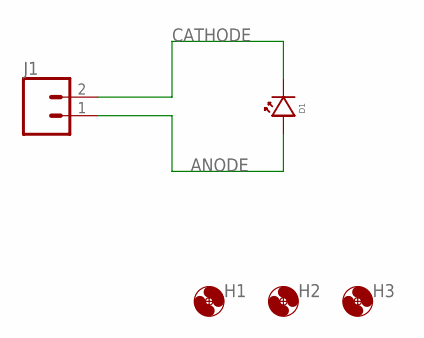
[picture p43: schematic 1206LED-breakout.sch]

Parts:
D1: LED1206; LED_1206
H1, H2, H3: MOUNTING_HOLE2_NP; 2_56
J1: CONN_021X02_NO_SILK; 1X02_NO_SILK

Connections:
ANODE: D1.ANODE, J1.1
CATHODE: D1.CATHODE, J1.2

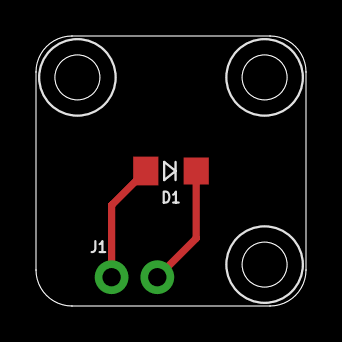
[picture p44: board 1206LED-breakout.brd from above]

Board: 2 copper layers, 15.0 x 15.0 mm, 5 parts (0 on the bottom side), 2 nets.

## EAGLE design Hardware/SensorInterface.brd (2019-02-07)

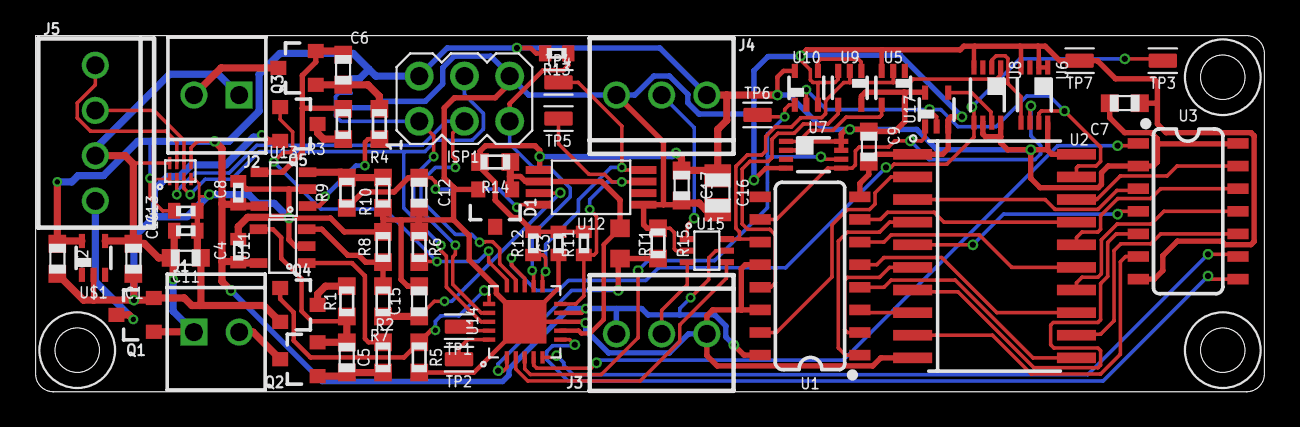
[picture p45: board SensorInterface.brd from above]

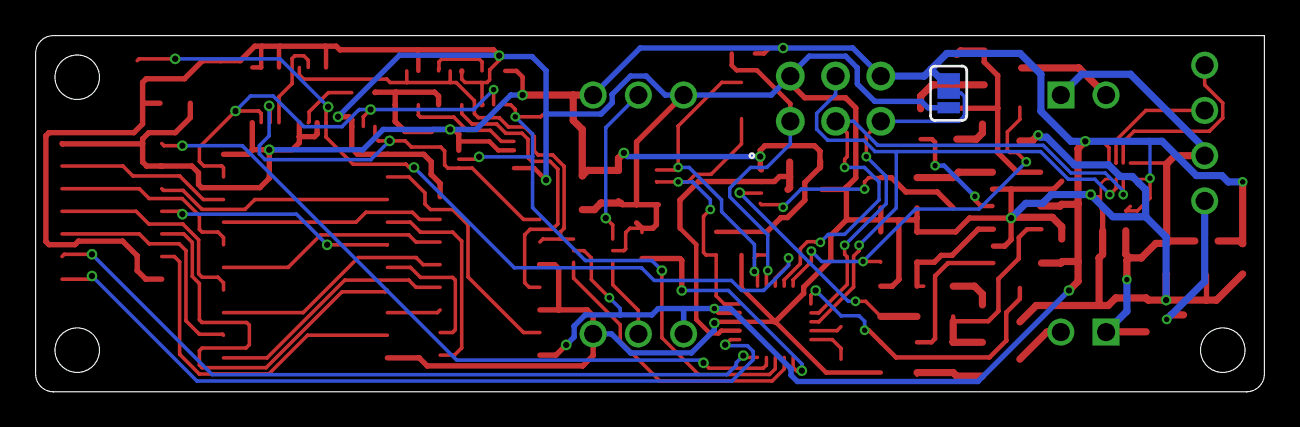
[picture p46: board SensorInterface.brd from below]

Board: 2 copper layers, 69.0 x 20.0 mm, 73 parts (2 on the bottom side), 64 nets.

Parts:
C1, C5, C6, C7, C9, C12, C15, C17: 0.1uF; C0603
C2, C11: 1uF; C0603
C3, C13, C14: 0.1uF; C0402
C4, C8: C0402
C16: 10uF; C0805
D1: SOT23-3
H1, H2, H3: 2_56
ISP1: AVRISP-6; AVRISP
J1, J2: 1X02_2.54_SCREWTERM
J3, J4: CONN_32.54_SCREW; 1X03_SCREW
J5: CONN_42.54_SCREW; 1X04_SCREW
JP0: JUMPER-SMT_3_1-NC_PASTE_SILK; SMT-JUMPER_3_1-NC_PASTE_SILK
LOGO1: OSHW-LOGOM; OSHW-LOGO-M
Q1, Q2, Q3, Q4, Q5: DMG3404; SOT23-3
R1, R3: 6.8; R0603
R2, R4: 220; R0603
R5, R6, R15: 10k; R0603
R7, R9: 3k; R0603
R8, R10: 1k; R0603
R11, R12, R13: 10k; R0402
R14: 4.7k; R0603
RT1: R0603
TP1, TP2, TP3, TP4, TP5, TP6, TP7: TESTPOINTRCU; TESTPOINT_0603
U1: SO16
U2: CD74HCT688DW; SO-20DW
U3: SN74HC164D; SO14
U5: DCK_R-PDSO-G5
U6, U7, U8: SN74LVC1G74DCU; DCU_(R-PDSO-G8)
U9, U10: SN74AHC1G86DCK; DCK_R-PDSO-G5
U11, U13: MCP6041; SOT23-5
U12: MCP47FEB22TTSOP; TTSOP_8
U14: QFN20
U15: SN74AUP1T157DCK; DCK_R-PDSO-G6
U16: TXS0102DQM; DQM_R-PX2SON-N8
U17: SN74AUP1G08DCK; DCK_R-PDSO-G5
U$1: TPS79733; DCK_R-PDSO-G5

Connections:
3V3: C2.1, C3.1, C4.1, C7.1, C8.1, C9.1, C13.1, C16.1, C17.1, ISP1.2, J3.3, J4.3, JP0.1, R11.2, R12.2, R13.2, R14.2, U1.16, U2.20, U3.2, U3.14, U5.5, U6.8, U7.2, U7.7, U7.8, U8.6, U8.8, U9.5, U10.5, U11.5, U12.1, U13.5, U14.9, U15.5, U16.1, U16.5, U17.5, U$1.5
!CLEAR: U3.9, U14.5
!COUNTRES: U9.1, U10.4
!F_IN: U5.4, U7.1
!INT: TP3.1, U8.5, U14.13
!P=Q: U2.19, U6.7, U10.2, U17.2
!RESET: ISP1.5, R13.1, U14.12
!SYNCRES: U1.10, U6.6, U7.5, U17.1
ADR_SEL: ISP1.1, JP0.2, U14.17
CLK: U3.8, U14.6
DATA: U3.1, U14.4
F_IN: U1.11, U5.2, U8.1, U9.2, U15.6
F_IN_0: J3.2, U15.3
F_IN_1: J4.2, U15.1
F_IN_SW: U14.2, U15.4
GND: C1.2, C2.2, C3.2, C4.2, C7.2, C8.2, C9.2, C11.2, C12.2, C13.2, C14.2, C15.2, C16.2, C17.2, D1.2, ISP1.6, J3.1, J4.1, JP0.3, Q1.2, Q4.2, Q5.2, R5.1, R6.1, R8.1, R10.1, R15.1, TP7.1, U1.8, U1.12, U1.14, U2.1, U2.10, U3.7, U5.3, U6.1, U6.2, U6.4, U7.4, U8.4, U9.3, U10.3, U11.2, U12.5, U13.2, U14.8, U14.EP, U15.2, U16.4, U17.3, U$1.2
INT_SET: U8.7, U17.4
LED1-: J1.P1, Q2.3
LED1_CTRL: Q4.1, R5.2, U14.16
LED2-: J2.P1, Q3.3
LED2_CTRL: Q5.1, R6.2, U14.15
unnamed: U1.15, U2.2
unnamed: U1.1, U2.4
unnamed: U1.2, U2.6
unnamed: U1.3, U2.8
unnamed: U1.4, U2.11
unnamed: U1.5, U2.13
unnamed: U1.6, U2.15
unnamed: U1.7, U2.17
unnamed: U2.3, U3.3
unnamed: U2.5, U3.4
unnamed: U2.7, U3.5
unnamed: U2.9, U3.6
unnamed: U2.12, U3.10
unnamed: U2.14, U3.11
unnamed: U2.16, U3.12
unnamed: U2.18, U3.13
unnamed: R7.2, R8.2, U11.3
unnamed: C6.2, Q3.2, R3.2, U13.4
unnamed: U6.5, U8.2
unnamed: C6.1, Q3.1, R4.1
unnamed: C5.2, Q2.2, R1.2, U11.4
unnamed: C5.1, Q2.1, R2.1
unnamed: R2.2, U11.1
unnamed: R4.2, U13.1
unnamed: Q5.3, R3.1
unnamed: Q4.3, R1.1
unnamed: R9.2, R10.2, U13.3
RCLK: U1.13, U9.4
RX: TP2.1, U14.20
SCL: R11.1, TP5.1, U12.7, U14.10
SCL_EXT: ISP1.3, U14.14, U16.2
SCL_EXT_HV: J5.4, U16.7
SDA: R12.1, TP4.1, U12.8, U14.11
SDA_EXT: ISP1.4, U14.18, U16.3
SDA_EXT_HV: J5.3, U16.6
THERM_SENSE: R15.2, RT1.2, U14.1
TX: TP1.1, U14.19
URES: TP6.1, U7.6, U10.1, U14.3
VIN+: C1.1, C11.1, C14.1, J1.P2, J2.P2, J5.2, Q1.1, U16.8, U$1.4
VIN-: J5.1, Q1.3
VREF: D1.1, R14.1, RT1.1, U12.2, U14.7
V_SET1: C15.1, R7.1, U12.3
V_SET2: C12.1, R9.1, U12.4

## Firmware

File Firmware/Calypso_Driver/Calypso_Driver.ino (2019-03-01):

/******************************************************************************
Calypso_Driver.cpp
Firmware for Calypso
Bobby Schulz @ Northern Widget LLC
2/19/2019
v0.0.0
https://github.com/NorthernWidget-Skunkworks/Project-Calypso

This firmware provides the low level control interface for the Calypso hardware 

"What is a scientist after all? It is a curious man looking through a keyhole, the keyhole of nature, trying to know what's going on."
-Jacques Cousteau

Distributed as-is; no warranty is given.
******************************************************************************/

#include <Wire.h>
#include <SlowSoftI2CMaster.h>
#define LED1 0  //Define values of LEDs for side indication
#define LED2 1

#define URES 4 //uReset on D4
#define LED1_CTRL 14 //LED 1 control pin on D14
#define LED2_CTRL 13 //LED 2 control pin on D13
#define DATA 5 //Data line to counter on D5
#define CLK 7 //Clock line to counter of D0
#define CLEAR 6 //Clear line to counter on D7
#define DONE 11 //Int line to comparator on D1 //FIX! Change name to INT??
#define F_IN_SW 3 //Input switch on D3
#define THERM_PIN A3 //Thermistor input on ADC3
#define SDA_SOFT PIN_C4
#define SCL_SOFT PIN_C5

#define ADR_DAC 0x60 //Address for DAC
#define ADR_SEL_PIN 15 //Digital pin 15 is used to test which device address should be used

#define VREF_VAL 0x000F //Set both referances to Vref (buffered)
#define SYS_STATUS_VAL
#define SYS_STATUS_REG 0x0A //Register which contains system status and gain info
#define VREF_REG 0x08 //Voltage referance set regitser 

#define LED0A 0x02
#define LED1A 0x04
#define COUNT 0x07
#define CTRL 0x00
#define TIME 0x09
#define SCALE 0x0B


#define READ 0x01
#define WRITE 0x00

uint16_t Res = 6800; //Resistance in mOhms of load resistor(s)
uint8_t Div = 19; //Division factor

uint8_t Config = 0; //Global config value

uint8_t Reg[22] = {0}; //Initialize registers

SlowSoftI2CMaster si = SlowSoftI2CMaster(SDA_SOFT, SCL_SOFT, true);  //Initialize software I2C  //FIX! Check pin values!

//FIX! Update values!
volatile uint8_t ADR = 0x40; //Use arbitraty address, change using generall call??
const uint8_t ADR_Alt = 0x41; //Alternative device address  //WARNING! When a #define is used instead, problems are caused

volatile bool StopFlag = false; //Used to indicate a stop condition 
volatile uint8_t RegID = 0; //Used to denote which register will be read from
volatile bool RepeatedStart = false; //Used to show if the start was repeated or not

volatile long TripTime = 0; //value used for measuring time of low pulse 
volatile bool NewData = false; //Used to test for new pulse data 

bool Busy = false; //Used to indicate when the device is taking a new sample

void setup() {
	Serial.begin(4800); //DEBUG!
	Reg[CTRL] = 0x00; //Set Config to POR value
	pinMode(LED1_CTRL, OUTPUT);
	pinMode(LED2_CTRL, OUTPUT);
	digitalWrite(LED1_CTRL, HIGH);
	digitalWrite(LED2_CTRL, HIGH); //Turn on LED switches 

	// pinMode(LED1_CTRL, OUTPUT);
	pinMode(DATA, OUTPUT);
	pinMode(CLK, OUTPUT);
	pinMode(CLEAR, OUTPUT);
	pinMode(URES, OUTPUT);
	pinMode(DONE, INPUT);
	pinMode(F_IN_SW, OUTPUT);
	digitalWrite(F_IN_SW, LOW); //default to input0
	digitalWrite(CLEAR, HIGH);
	pinMode(ADR_SEL_PIN, INPUT_PULLUP); 
	if(!digitalRead(ADR_SEL_PIN)) ADR = ADR_Alt; //If solder jumper is bridged, use alternate address //DEBUG!
  	Wire.begin(ADR);  //Begin slave I2C

  	// Wire.onAddrReceive(addressEvent); // register event
	Wire.onRequest(requestEvent);     // register event
	Wire.onReceive(receiveEvent);
	// Wire.onStop(stopEvent);

	si.i2c_init(); //Begin I2C master

	si.i2c_start((ADR_DAC << 1) | WRITE);  //Set voltage referance
	si.i2c_write((VREF_REG << 3) | WRITE); 
	si.i2c_write(VREF_VAL >> 8);  
	si.i2c_write(VREF_VAL & 0xFF);
	si.i2c_stop();

	attachInterrupt(digitalPinToInterrupt(11), Trip, CHANGE);
	//Set DAC Gain???? FIX!
}

void loop() {
	if((Reg[CTRL] & 0x80) == 0x80 && Busy == false && ReadBit(Reg[CTRL], 6)) {  //Test if Sample/rdy bit is set and not already taking a sample, and device is enabled //FIX! Enable condition??
		Busy = true; //Set busy flag and start sample
		//Add sample procedure!
		//Set LEDs
		//Set Counter
		//Clear counter
		//Start timer
		//release counter
		Serial.print("SET");
		// noInterrupts(); //FIX!!
		// Serial.print(Reg[LED0A], HEX); //DEBUG!
		// Serial.print(Reg[LED0A + 1], HEX); //DEBUG!
		TripTime = 0; //Clear timing coutner 
		digitalWrite(URES, LOW); //Hold system in reset
		digitalWrite(LED1_CTRL, ReadBit(Reg[CTRL], 1)); //Set LED1 transistor from control reg
		digitalWrite(LED2_CTRL, ReadBit(Reg[CTRL], 2)); //Set LED2 transistor from control reg
		digitalWrite(F_IN_SW, ReadBit(Reg[CTRL], 0)); //Set input switch with value from control reg
		SetCurrent((Reg[LED0A + 1] << 8) | Reg[LED0A], 0); //Set LED0 to current 0
		SetCurrent((Reg[LED1A + 1] << 8) | Reg[LED1A], 1); //Set LED1 to current 1

		SetCount(Reg[COUNT]); //Set the count of the system
		digitalWrite(URES, HIGH); //Release counter, begin operation
		NewData = false; //Clear data reg
		// interrupts(); //re-enable interrupts to get count //FIX!
		// Reg[CTRL] = Reg[CTRL] & 0x7F; //DEBUG! //Clear sample/rdy bit
	}
	// Serial.println(Reg[CTRL]); //DEBUG!
	if(NewData) {
		//Load new data into registers
		//Set ready bit in control reg 
		NewData = false;
		Busy = false;
		long Temp = 0;
		Temp = TripTime/8; //Scale to rollovers
		Reg[TIME] = Temp & 0xFF; //LSB of time val
		Reg[TIME + 1] = (Temp >> 8) & 0xFF; //Middle byte of time val
		Reg[TIME + 2] = (Temp >> 16) & 0xFF; //MSB of time val
		// Serial.println(Reg[TIME]); //DEBUG!
		Serial.println("DONE");
		Reg[CTRL] = Reg[CTRL] & 0x7F; //Clear sample/rdy bit
	}

	//Update general prams on every loop
	digitalWrite(LED1_CTRL, ReadBit(Reg[CTRL], 1)); //Set LED1 transistor from control reg
	digitalWrite(LED2_CTRL, ReadBit(Reg[CTRL], 2)); //Set LED2 transistor from control reg
	digitalWrite(F_IN_SW, ReadBit(Reg[CTRL], 0)); //Set input switch with value from control reg
	SetCurrent((Reg[LED0A + 1] << 8) | Reg[LED0A], 0); //Set LED0 to current 0
	SetCurrent((Reg[LED1A + 1] << 8) | Reg[LED1A], 1); //Set LED1 to current 1
	delay(1); //FIX! Keep?
}

//Current given in uA
int SetCurrent(long Current, bool Side) //Set current drive for led, use Side to set which LED to set, 0 for LED1, 1 for LED2
{
	//ADD VOLTAGE DIVIDER VALUE!!??
	//RETURN BAD VALUE IF SET OUTSIDE OF RANGE!??
	uint16_t Voltage = 0;
	// if(ReadBit(Regs[0x06], 1) == 1) {
	si.i2c_start((ADR_DAC << 1) | WRITE);
	si.i2c_write((0x0A << 3) | 0b000); //Write to gain and status reg
	// si.i2c_write(ReadBit(Reg[0x06], 1) << (Side + 0x08)); //Set gain bit with the appropriate value (LED control reg, bit 1)
	// si.i2c_write(ReadBit(Reg[0x06], 1) << Side); //Set both to 2x gain //DEBUG!!!!
	if(ReadBit(Reg[0x06], 1)) si.i2c_write(0x03); //Set gain = 2x
	else si.i2c_write(0x00); //Set gain = 1x
	si.i2c_write(0x00); //DEBUG!
	si.i2c_stop();
	// }
	if(ReadBit(Reg[0x06], 0) == 1) { //If mode bit is set, use direct pass through
		Voltage = Current; //DEBUG!
	}
	else {
		Voltage = ((Current*Res)/500000)*Div; //Determine current set from load resistor 500 = 4096/2048000, bits/uV range
	}
	// Serial.print("VOLT"); //DEBUG!
	// Serial.print(Voltage); //DEBUG!
	si.i2c_start((ADR_DAC << 1) | WRITE); 
	si.i2c_write((Side << 3) | 0b000); //Write to reg 0 vs 1 depending on which DAC you want to write to 
	si.i2c_write(Voltage >> 8); //Write LSB
	si.i2c_write(Voltage & 0xFF); //Write MSB
	si.i2c_stop();
	//FIX! Return???
}

void SetCount(uint8_t Val)
{	//FIX! REPLACE!!
// 	bool Dummy = false; 
// 	DDRB = DDRB | 0x01; //Set pin PB0 as output  //DEBUG!
// 	DDRA = DDRA | 0x28; //Set pin PA5 and pin PA3 as output  //DEBUG!
// 	PORTA = PORTA | 0x08; //Turn Clear Off
// 	PORTA = PORTA & 0xDF; //Clear PA5 
// 	// Val = Val << 0x05; //Offset to allign with PORTA
	for(int i = 7; i >= 0; i--) {
		//FIX!!!!!!!!!!!!!!
// 		//FAST MODE
// 		PORTB = PORTB & 0xFE; //Clear bit, drive clock low  //DEBUG!
// 		asm("nop \n"); //pause for one clock cycle
// //		 PORTA = PORTA | ((Val >> i) & 0x01 ) << 0x05;  //DEBUG!
//     PORTA = PORTA & 0xDF;
// 		PORTA = PORTA | (Val >> 0x02) & 0x20;  //DEBUG!
// 		//// PORTA = PORTA | (Val  << (0x05 + i)) & 0x20;  //DEBUG!
// 		asm("nop \n"); //pause for one clock cycle
// 		PORTB = PORTB | 0x01; //Set bit, drive clock high  //DEBUG!
// 		asm("nop \n"); //pause for one clock cycle
// 		Val = Val << 0x01; //Shift to new val


		 digitalWrite(CLK, LOW); //Set clock low
		 digitalWrite(DATA, (Val >> i) & 0x01); //Write LSB to DATA pin
		 digitalWrite(CLK, HIGH); //Clock values in on rising edge
	}
}

void ClearCount()
{
	digitalWrite(CLEAR, LOW);
	delayMicroseconds(1);
	// delay(1); //Wait for clear to take place
	digitalWrite(CLEAR, HIGH); //Return to nominal value
}

void SplitAndLoad(uint8_t Pos, unsigned int Val) //Write 16 bits
{
	uint8_t Len = sizeof(Val);
	for(int i = Pos; i < Pos + Len; i++) {
		Reg[i] = (Val >> (i - Pos)*8) & 0xFF; //Pullout the next byte
	}
}

void SplitAndLoad(uint8_t Pos, long Val)  //Write 32 bits  //FIX! Needed?
{
	uint8_t Len = sizeof(Val);
	for(int i = Pos; i < Pos + Len; i++) {
		Reg[i] = (Val >> (i - Pos)*8) & 0xFF; //Pullout the next byte
	}
}

boolean addressEvent(uint16_t address, uint8_t count)
{
	RepeatedStart = (count > 0 ? true : false);
	return true; // send ACK to master
}

void requestEvent()
{	
	//Allow for repeated start condition 
	if(RepeatedStart) {  //FIX! Make repeated start actually work!
		for(int i = 0; i < 2; i++) {
			Wire.write(Reg[RegID + i]);
		}
	}
	else {
		Wire.write(Reg[RegID]);
	}
}

void receiveEvent(int DataLen) 
{
    //Write data to appropriate location
    if(DataLen == 2){
	    //Remove while loop?? 
	    while(Wire.available() < 2); //Only option for writing would be register address, and single 8 bit value
	    uint8_t Pos = Wire.read();
	    uint8_t Val = Wire.read();
	    //Check for validity of write??
	    Reg[Pos] = Val; //Set register value
	}

	if(DataLen == 1){
		RegID = Wire.read(); //Read in the register ID to be used for subsequent read
	}
}

void stopEvent() 
{
	StopFlag = true;
	//End comunication
}

void Trip(void)
{
	TripTime = micros() - TripTime; //Measure delta period
	if(digitalRead(11)) NewData = true; //Set new data flag only on rising edge
}

bool ReadBit(uint8_t Val, uint8_t Pos)  //Returns the value of the specified position in the register
{
	return (Val >> Pos) & 0x01;
}

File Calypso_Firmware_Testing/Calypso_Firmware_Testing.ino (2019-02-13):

//Calypso_Firmware_Testing.ino
#include <SlowSoftWire.h> 

SlowSoftWire Wire = SlowSoftWire(2, 3);
#define MCP4726_CMD_WRITEDAC            (0x40)  // Writes data to the DAC
#define MCP4726_CMD_WRITEDACEEPROM      (0x60)  // Writes data to the DAC and the EEPROM (persisting the assigned value after reset)

#define LED1 0  //Define values of LEDs for side indication
#define LED2 1

#define URES 9 //uReset on D9
#define LED1_CTRL 10 //LED 1 control pin on D10
#define LED2_CTRL 10 //LED 2 control pin on D10 (Tied together for demo!!!!!!)
#define DATA 5 //Data line to counter on D5
#define CLK 0 //Clock line to counter of D0
#define CLEAR 7 //Clear line to counter on D7
#define DONE 1 //Int line to comparator on D1

// #define DAC_1_ADR 0x63  //Address for DAC that controls LED1 current
// #define DAC_2_ADR 0x62  //Address for DAC that controls LED2 current
uint8_t DAC_Adr[2] = {0x63, 0x62}; //Address for LED1 DAC, LED2 DAC

uint16_t Res = 100; //Resistance in Ohms of load resistor(s)
uint8_t Div = 2; //Division factor

void setup() {
  // put your setup code here, to run once:
  Wire.begin();
  // pinMode(9, OUTPUT);
  pinMode(10, OUTPUT);
  // digitalWrite(9, HIGH);
  digitalWrite(10, HIGH); //Turn on LED switches 

  pinMode(LED1_CTRL, OUTPUT);
  pinMode(DATA, OUTPUT);
  pinMode(CLK, OUTPUT);
  pinMode(CLEAR, OUTPUT);
  pinMode(URES, OUTPUT);
  pinMode(DONE, INPUT);
}

void loop() {
  // put your main code here, to run repeatedly:
  // for(int i = 0; i < 4096; i += 10) {
  // 	SetVoltageRaw(i, LED1);
  // 	SetVoltageRaw(4095 - i, LED2);
  // }
  // for(int i = 4095; i > 0; i-= 10) {
  // 	SetVoltageRaw(i, LED1);
  // 	SetVoltageRaw(4095 - i, LED2);
  // }

  // SetVoltageRaw(0, LED1);
  // SetVoltageRaw(0, LED2);
  // delay(1000);
    digitalWrite(LED1_CTRL, HIGH);
//    SetVoltageRaw(128, LED1);
//    delay(2000);
//    SetVoltageRaw(256, LED1);
//    delay(2000);
//    SetVoltageRaw(512, LED1);
//    delay(2000);
//    SetVoltageRaw(1024, LED1);
//    delay(2000);
//    SetVoltageRaw(2048, LED1);
//    delay(2000);
    SetVoltageRaw(4095, LED1);
    delay(2000);
//  ClearCount();
//  SetCount(10);
//  digitalWrite(URES, LOW);
//  delayMicroseconds(300);
//  digitalWrite(URES, HIGH);
//  delay(100); //DEBUG!

  // while(1);
  // delay(10);
  // ClearCount();
  // delay(10);
  // SetCount(2);
  // delay(10);
  // ClearCount();
  // delay(10);
}

void LED_Demo()  //Test function only!
{
	for(int i = 0; i < 4096; i += 10) {
		SetVoltageRaw(i, LED1);
		SetVoltageRaw(4095 - i, LED2);
	}
	for(int i = 4095; i > 0; i-= 10) {
		SetVoltageRaw(i, LED1);
		SetVoltageRaw(4095 - i, LED2);
	}
}

//Current given in uA
int SetCurrent(long Current, bool Side) //Set current drive for led, use Side to set which LED to set, 0 for LED1, 1 for LED2
{
	//ADD VOLTAGE DIVIDER VALUE!!??
	//RETURN BAD VALUE IF SET OUTSIDE OF RANGE!??
	uint16_t Voltage = ((Current*Res)/806)*Div; //Determine current set from load resistor 806 = 4096/3300000, bits/uV range
	Wire.beginTransmission(DAC_Adr[Side]);
	Wire.write(MCP4726_CMD_WRITEDAC);
	Wire.write(Voltage / 16);                   // Upper data bits          (D11.D10.D9.D8.D7.D6.D5.D4)
	Wire.write((Voltage % 16) << 4);            // Lower data bits          (D3.D2.D1.D0.x.x.x.x)
	Wire.endTransmission();
}

//Set bit value
int SetVoltageRaw(uint16_t Val, bool Side) 
{
	//ADD VOLTAGE DIVIDER VALUE!!??
	//RETURN BAD VALUE IF SET OUTSIDE OF RANGE!??
	// uint16_t Voltage = ((Current*Res)/806)*Div; //Determine current set from load resistor 806 = 4096/3300000, bits/uV range
	Wire.beginTransmission(DAC_Adr[Side]);
	Wire.write(MCP4726_CMD_WRITEDAC);
	Wire.write(Val / 16);                   // Upper data bits          (D11.D10.D9.D8.D7.D6.D5.D4)
	Wire.write((Val % 16) << 4);            // Lower data bits          (D3.D2.D1.D0.x.x.x.x)
	Wire.endTransmission();
}
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

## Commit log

2018-05-16 Added LED current drive simulations
2018-05-29 Initial Schematic Layout, Edits to simulation
    Initial schematic layout complete, needs verification, made edits to the simulator on the LED current drive to both simulate the RC compensator network and the input voltage division
    [SensorInterface.sch]
2018-05-31 Updated frame info
    [SensorInterface.sch]
2018-10-15 Cleanup and added documentation (design drawings)
    [SensorInterface.sch]
2018-12-17 Edits to schematic and simulations
    [SensorInterface.brd, SensorInterface.sch]
2018-12-18 Eagle files in same directory
    [SensorInterface.brd]
2018-12-18 +1 detector, MUX, 3V3 labels
    [SensorInterface.brd, SensorInterface.sch]
2018-12-18 LED system laid out (mostly)
    [SensorInterface.brd]
2018-12-18 Initial routing complete with DRC
    [SensorInterface.brd]
2018-12-24 Silkscreen for initial prototype
    [SensorInterface.brd, SensorInterface.sch]
2018-12-24 Pin labels
    [SensorInterface.brd]
2019-01-02 Post-review update * Shortened analog feedback and power traces * Checked trace widths for uniformity and appropriateness * Added 5V/3.3V level conversion * Pull-ups on I2C (internal) and RESET
    [SensorInterface.brd, SensorInterface.sch]
2019-01-02 Board cleanup
    Cleaned up layout, increased silkscreen width, increased power path width, changed layout of 3v3 reg
2019-01-04 Actual board cleanup
    Fixed empty push issue, see last commit
    [SensorInterface.brd]
2019-01-04 Schulz to board attribution
    [SensorInterface.brd]
2019-01-04 thicker power path traces
    [SensorInterface.brd]
2019-01-04 Added gerbers, minor cleanup, v0.0.0 submitted to fab
    Cleaned up board and made some minor changes to decoupling capacitor layout, adjusted some traces. Generated gerbers and submitted boards for v0.0
    [SensorInterface.brd, SensorInterface.sch]
2019-01-16 Move and define caps
    [SensorInterface.brd, SensorInterface.sch]
2019-01-16 Trace updates for caps
    [SensorInterface.brd]
2019-01-19 first draft
    [TSL238T-breakout.brd, TSL238T-breakout.sch]
2019-01-19 Labels, 3rd hole
    [TSL238T-breakout.brd, TSL238T-breakout.sch]
2019-01-19 re-center detector
    [TSL238T-breakout.brd]
2019-01-19 rm unnecessary label
    [TSL238T-breakout.brd]
2019-01-19 LED, also 15mm square
    [1206LED-breakout.brd, 1206LED-breakout.sch]
2019-01-30 Updated breakouts and main board, schematic v0.1 updates
    Updated schematic for main unit to v0.1, incorporating updates from testing of v0.0 unit
    Minor updates to breakout boards, adding passives and updating components
    [1206LED-breakout.brd, 1206LED-breakout.sch, SensorInterface.brd, SensorInterface.sch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]
2019-01-31 Routed; DRC passed
    [SensorInterface.brd]
2019-02-01 Reroute initial stage
    [SensorInterface.brd, SensorInterface.sch]
2019-02-02 Continued layout update
    Layout is functional for v0.1, review and clean up still required but functional layout completed
    [SensorInterface.brd, SensorInterface.sch]
2019-02-04 Mounting hole in NE corner
    [SensorInterface.brd, SensorInterface.sch]
2019-02-04 Added mount holes, cleaned up sim
    Cleaned up simulation files and gitignore, added mounting holes to board
    [SensorInterface.brd, SensorInterface.sch]
2019-02-04 Layout cleanup ready for review
    [SensorInterface.brd, SensorInterface.sch]
2019-02-04 SE corner hole added
    [SensorInterface.brd, SensorInterface.sch]
2019-02-06 Minor cleanup, generated gerbers
    Cleaned up silkscreen on board and generated gerbers for main board and breakouts
    [SensorInterface.brd]
2019-02-07 Added PDFs and replaced OSHW logo
    Added PDFs for board (clean) and schematic (nearly clean), also replaced the OSHW logo with one from ColdSilicon which uses the correct layer
    [SensorInterface.brd, SensorInterface.sch]
2019-02-13 Added preliminary driver interface
    Added in progress Calypso firmware driver, also added additional labeling to schematic for sensor interface
    [SensorInterface.sch]
2019-02-19 Continued firmware dev and testing
    Tested current control over I2C, tested counting and count setting, system able to return pulse time values over I2C
2019-02-21 Improved serial interface, added basic sweep function
    Several improvements and bug fixes to the serial interface, still need to deal with the lockup issue on the firmware side. Also added dimensional documentation to the TSL238T breakout
    [TSL238T-breakout.brd]
2019-02-27 Cleaned up schematic for report
    [SensorInterface.sch]
2020-05-01 stencil mount and optics mount
    [Calypso_OpticsMount_v2.STL, StencilMount_Calypso.STL]
2023-07-25 Assembly instructions: Senior Design Prototype (2018)
2023-07-25 Senior Design 2018 archive Design files from the working metal-box prototype Here, included to document this design phase
    [3D Printed Part_notched_FINAL.SLDPRT, Metal Box Assembly.SLDASM, Metal Box Top.SLDPRT, Metal Box.SLDPRT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]
2023-07-25 Bill of materials
    [Calypso-BoM_SrD-2018.csv]
2023-07-26 Formazin standard, varying concentration.
    [Summarized Calibration Data.xlsx]
2023-07-26 Move old Hardware into Sr Design folder.
    [3D Printed Part_notched_FINAL.SLDPRT, Calypso-BoM_SrD-2018.csv, Metal Box Assembly.SLDASM, Metal Box Top.SLDPRT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]
2023-07-26 Add summary (first part) and LED+detector fig.
2023-07-26 Clarify LED-beam figure caption.
2023-07-26 LED mount
2023-07-26 CAD sensor and mount.
2023-07-26 Photo of the 3-D printed mount and custom PCB.
2023-07-26 Sensor characterization using Formazin standards.

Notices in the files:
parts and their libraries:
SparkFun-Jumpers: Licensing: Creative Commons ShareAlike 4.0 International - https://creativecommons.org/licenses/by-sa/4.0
